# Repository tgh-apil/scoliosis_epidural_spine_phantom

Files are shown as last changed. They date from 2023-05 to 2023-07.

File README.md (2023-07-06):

# APIL Scoliotic Spine Epidural Phantom

scoliotic spine phantom gel and spine upright

3D Printed thoracic and lumbar (T6 - L2) scoliotic spine based on CT data.  Our scoliotic spine phantom is encased in an synthetic, shelf-stable gel which has a realistic tactile feel to human muscle and is echogenic.  We can augment the echogenic properties to be transparent (clear gel, pictured above) to mimicing that of biological tissue (opaque) based on the learning objective. Additionally, the Scoliotic Spine Epidural Phantom contains an echogenic faux-thecal sac to replicate loss-of resistance on puncture.  The faux-thecal sca can be inflated with water to simulate spinal fluid. 

This model was developed at the [Lynn & Arnold Irwin Advanced Perioperative Imaging Lab](https://apil.ca), Toronto General Hospital, University Health Network.

# Purchasing Information
To purchase this phantom, please email <apil@uhn.ca> and a represtative will be in touch with you with more details.

**A purchased phantom contains the following**:

1. Fully assembled scoliotic spine phantom.
2. Custom table clamp to hold phantom to tabe surface

# Ultrasound Images
Coming soon

# Care and Maintenance
1. Apply generous amount of ultrasound gel to surface of phantom.
2. Inflate thecal sac with water and ensure quickturn locks are closed

# Materials & Equipment

## Hardware

- M5*14 pins
- 4 x M4*16 Bolts
- 4 x M4*20 Bolts
- Quick-turn Lock
- 8 mm ID Silicone Tubing (as low durometer as possible)
- Tube Fittings

## Printing Equipment

- Polylactic Acid (PLA)
- Bridge Nylon
- Fused Deposition Modelling 3D printer

## Casting Equipment

- Ballistics Gel
  - Gelatin #3 from [Humimic Medical](https://humimic.com/product/gelatin-3-medical-gel-by-the-pound/)
- Graphite Powder (optional)
  - used to replicate echogenic scatter of muscle
- Slowcooker
- Two-part Platinum Cure Silicone Rubber (or equivalent)
  - Available from [Smooth-On](https://www.smooth-on.com/products/dragon-skin-30/)
- Degas Chamber (Optional)

# Assembly Instructions

## Printing

This repo includes **stl** files for each printed part.

In general, we use the following settings for *all* parts of this phantom:

<table>
    <tr>
        <td><b>Material</b></td>
        <td><b>Colour</b></td>
        <td><b>Nozzle Temp (C)</b></td>
        <td><b>Bed Temp (C)</b></td>
        <td><b>Infill (%)</b></td>
        <td><b>Perimiters (#)</b></td>
    </tr>
    <tr>
        <td>PLA</td>
        <td>White</td>
        <td>210.0</td>
        <td>60.0</td>
        <td>10.0</td>
        <td>2</td>
    </tr>
    <tr>
        <td>Bridge Nylon</td>
        <td>Natural</td>
        <td>250.0</td>
        <td>80.0</td>
        <td>15.0</td>
        <td>3</td>
    </tr>
</table>

## Silicone Casting

### Silicone Mold Casting

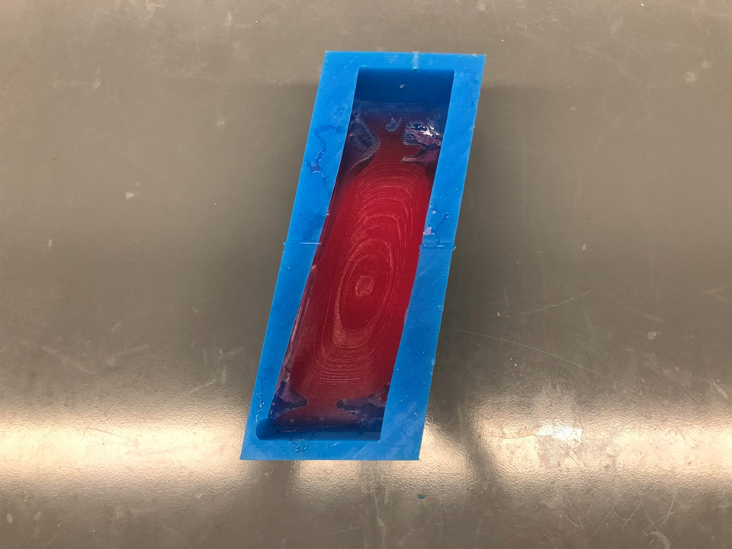
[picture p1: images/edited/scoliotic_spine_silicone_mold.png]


1. Print all components in the directory */molds/* using the PLA printing settings outlined above.
2. Assemble mold parts 1, 2 and inner components together using M5*14 pins.
3. Mix **1300 g** of silicone according to manufacturers instructions.
    - Degassing the silicone is encoraged, but optional.
    - Adding colourant to silicone is optional.
4. Pour all silicone into the assembled mold.
5. Allow silicone to cure according to manufacturer's instructions.
6. Carefully disassmble the mold and release the silicone.
   - **NOTE:** This step can be very difficult.  Procede with caution and patience to avoid damaging the silicone shell.

## 3D Printing Components

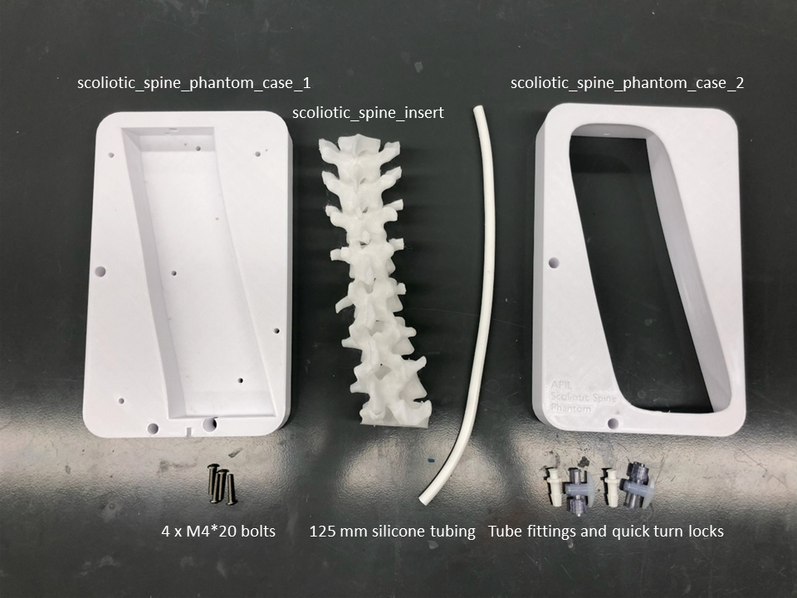
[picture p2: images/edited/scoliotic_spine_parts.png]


1. Print all components in the directory */scoliotic_spine_insert/* using the Bridge printing settings outlined above.
2. Print all components in the directory */case/* using the PLA printing settings outlined above.
3. Carefully remove **all** supports from the part when complete.

## Ballistics Gel Casting

1. **CAUTION:** Use appropriate heat-proof gloves when working with liquefied ballistic gel and/or heat gun.
2. **CAUTION:** work **only** in a very well ventilated area.  A fumehood is *highly* recommended.

### Ballistics Gel Casting

1. Melt at least **1000 g** gel in crockpot @ 105C - 115C (approx. 225F - 240F).
2. If the gel does not contain graphite powder, slowly add graphite powder into fully liquefied mixture until saturated.
   1. For this phantom, this step is optional.  You can leave it clear if the learning objective is to insert an epidural without the use of ultrasound.
3. Thread a length of silicone tubing through the scoliotic sipne to replicate the thecal sac.  The length should be just enough to reach end-to-end of the scoliotic spine.
4. Anchor scoliotic spine insert and thecal sac silicone tube into the silicone mold with 4 x M4*16 bolts.
5. Pour gel into mold until the gel is flush with the top of the spine insert
6. Allow gel to fully cool before removal from silicone molds.
7. Remove previously installed silicone tube.
8. Install a new silicone tube measuring 125 mm.
   1. we use a longer silicone tube in this step so the ends of the tubing extend well past the case for ease of access.

## Phantom Assembly

1. Squeeze the gel and scoliotic spine through the printed lid of the case(scoliotic_spine_phantom_case_1).
2. Attach lid with the scoliotic spine to the base of the case (scoliotic_spine_phantom_case_2).
3. Thread the ends of silicone tubing through the holes provided in the base of the case
4. Join the lid and base together using 4 x M4*20 bolts.
5. Attach a tube fitting to each end of the silicone tube.
6. Attach a quick-turn lock to each end of the tube fittings.

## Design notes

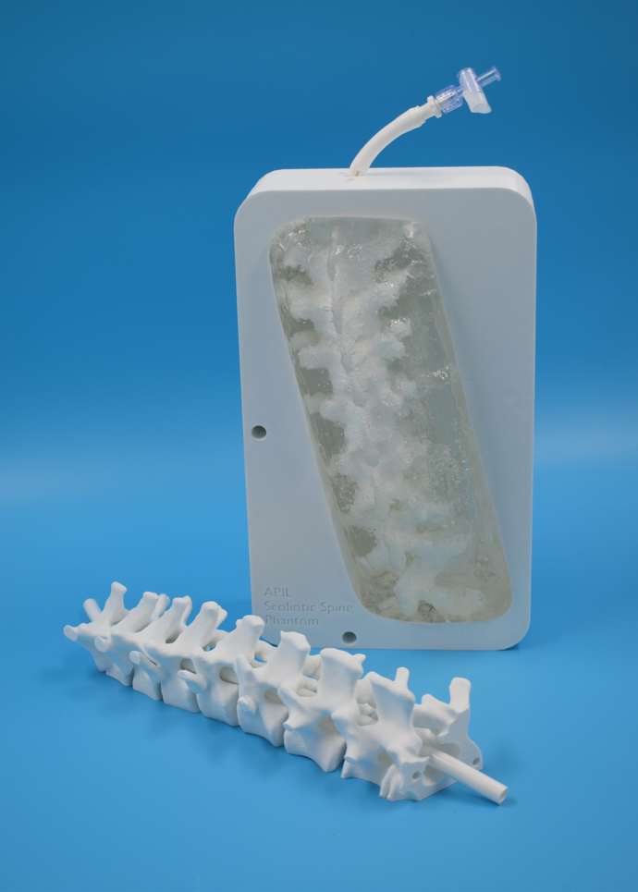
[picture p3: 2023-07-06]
images/edited/scoliotic spine phantom gel and spine upright.png

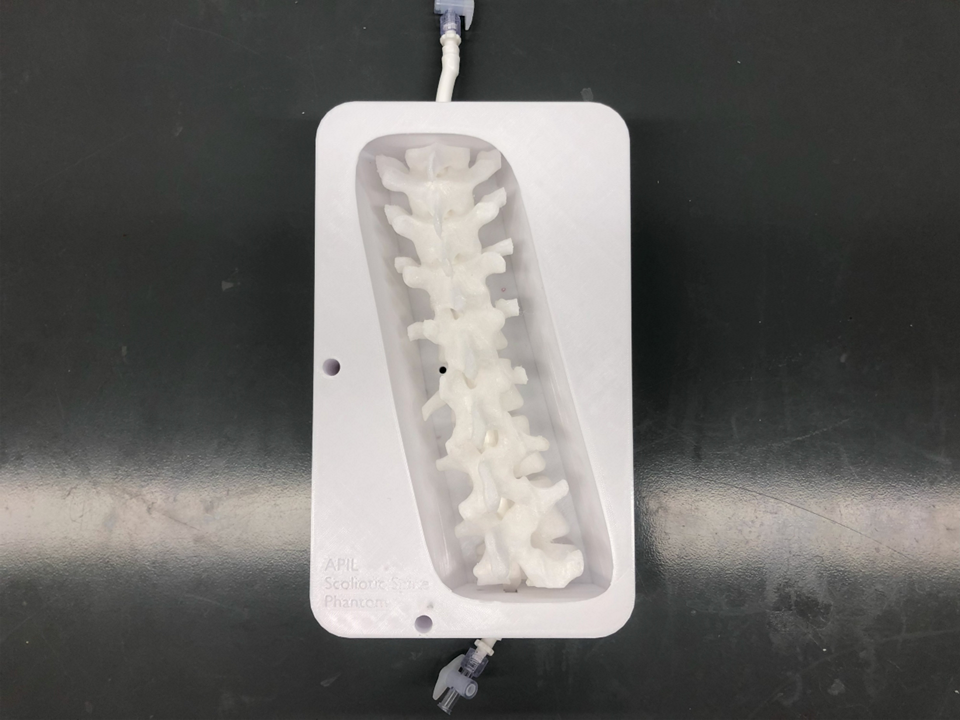
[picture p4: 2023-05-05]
images/edited/scoliotic_spine_phantom_no_gel.png

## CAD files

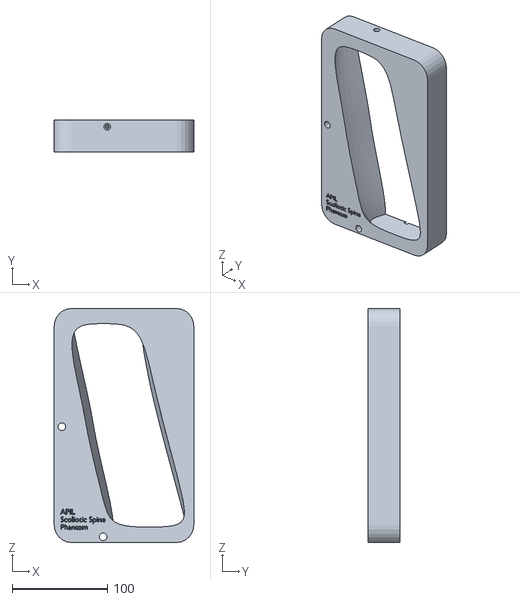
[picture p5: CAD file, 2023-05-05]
case/scoliotic_spine_phantom_case_1.stl
146.2 x 33.6 x 245.2

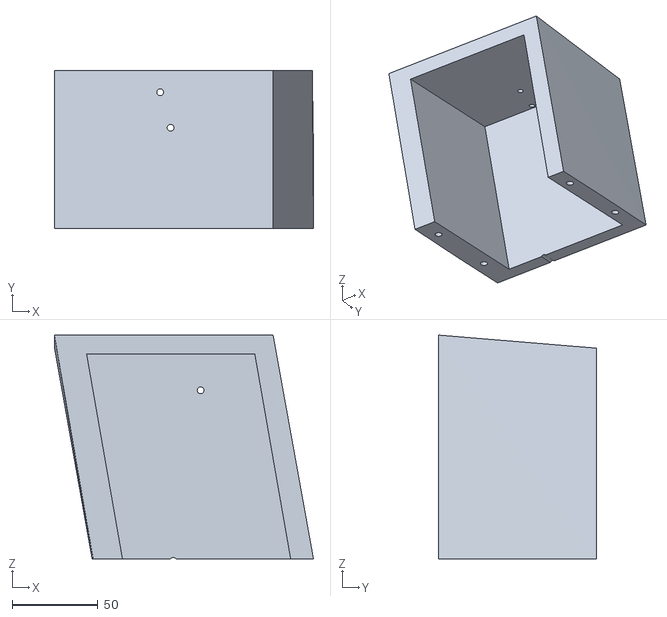
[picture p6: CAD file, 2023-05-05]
molds/scoliotic_spine_phantom_mold_1.stl
151.4 x 92.5 x 130.8

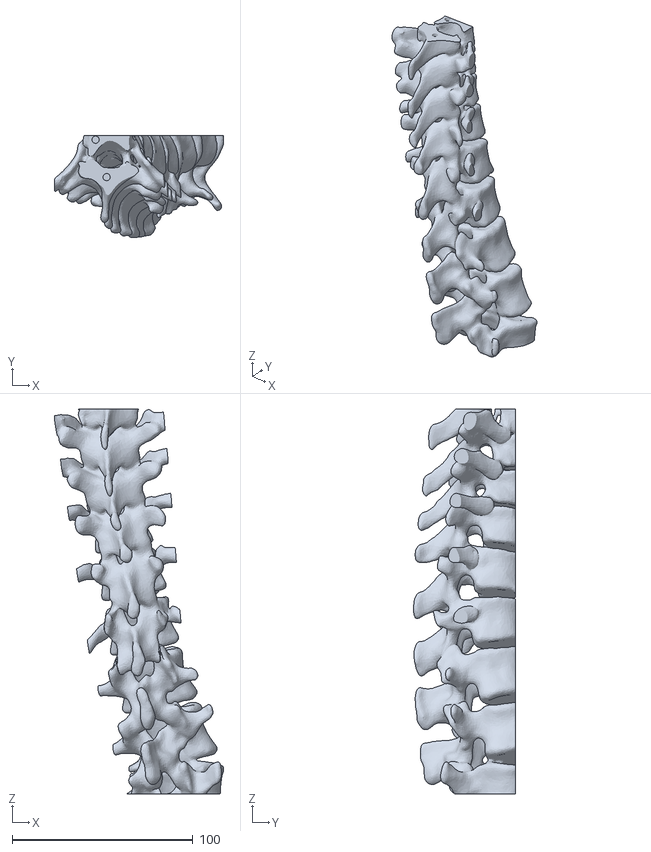
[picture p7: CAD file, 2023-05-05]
scoliotic_spine_insert/scoliotic_spine_insert.stl
93.9 x 56.8 x 213.3

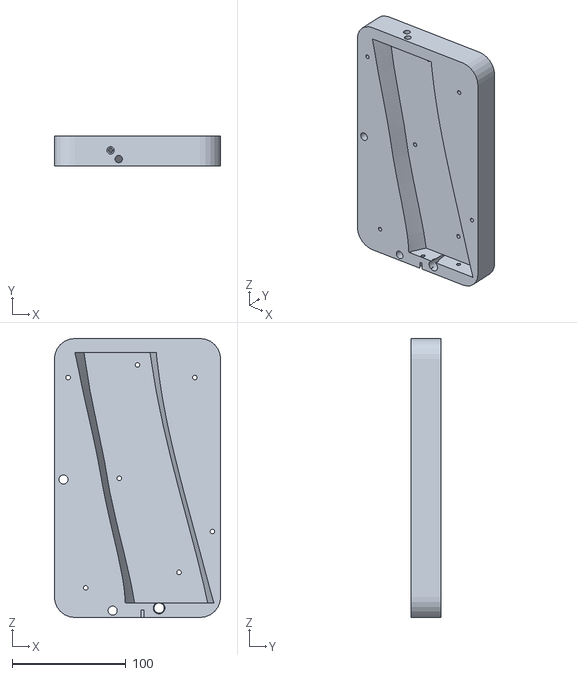
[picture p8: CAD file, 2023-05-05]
case/scoliotic_spine_phantom_case_2.stl
146.2 x 25.9 x 245.2

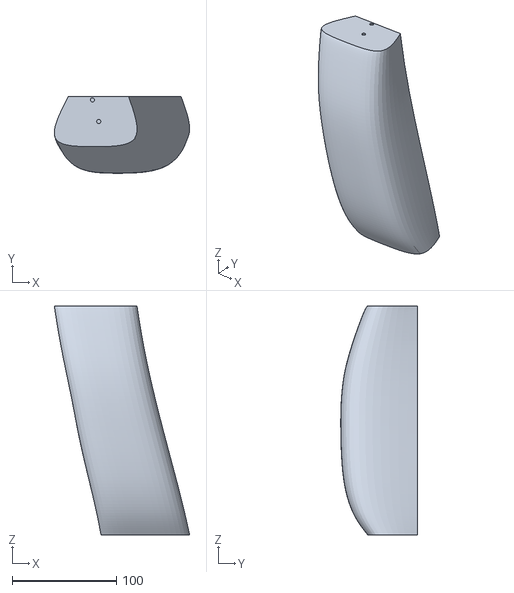
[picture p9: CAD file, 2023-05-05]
molds/scoliotic_spine_phantom_mold_inner.stl
130.0 x 73.5 x 220.0

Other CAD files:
molds/scoliotic_spine_phantom_mold_2.stl
